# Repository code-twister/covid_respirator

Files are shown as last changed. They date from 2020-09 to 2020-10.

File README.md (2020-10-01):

# code-twister ventilator

## The idea

Following the shortages of ventilators in countries severely affected by covid 19 this project aimed to give a relatively cheap solution to help those people who have no other option.

The design itself is intended to be free for anyone to use, update, create and even sell the machines.

There are a lot of other open source ventilators to choose from, hopefully this design will also help.

DISCLAIMER: This project and all related resources are provided without any guaranties, and you should use it at your own risk. Please make sure you respect the law in your country related to medical equipment.

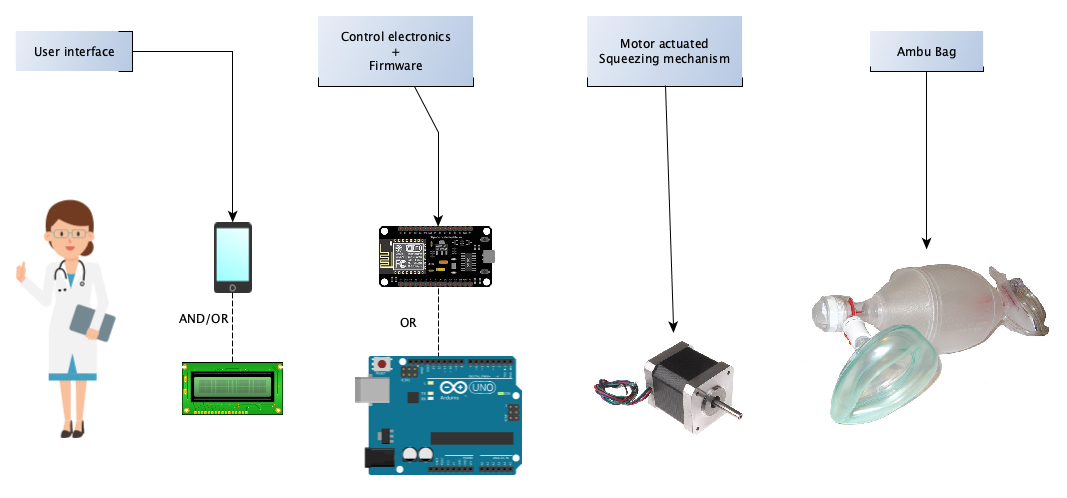
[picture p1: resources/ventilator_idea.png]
Ventilator idea The basic ventilator idea


### Things considered
 - Parts should be readily available (e.g. 3d printer parts).
 - Custom components should be 3d printable or created using common hand tools.
 - Use **ambu bag** as air delivery to make sure it's safe for patients.
 - A way to set parameters like speeds, volume, pressure limits, sigh feature.
 - Ambu bag must be easy to replace by medical personnel.

## Ventilator prototype

(http://www.youtube.com/watch?v=9s-Q_Xbm_GY "Prototype")

**Actual build:**

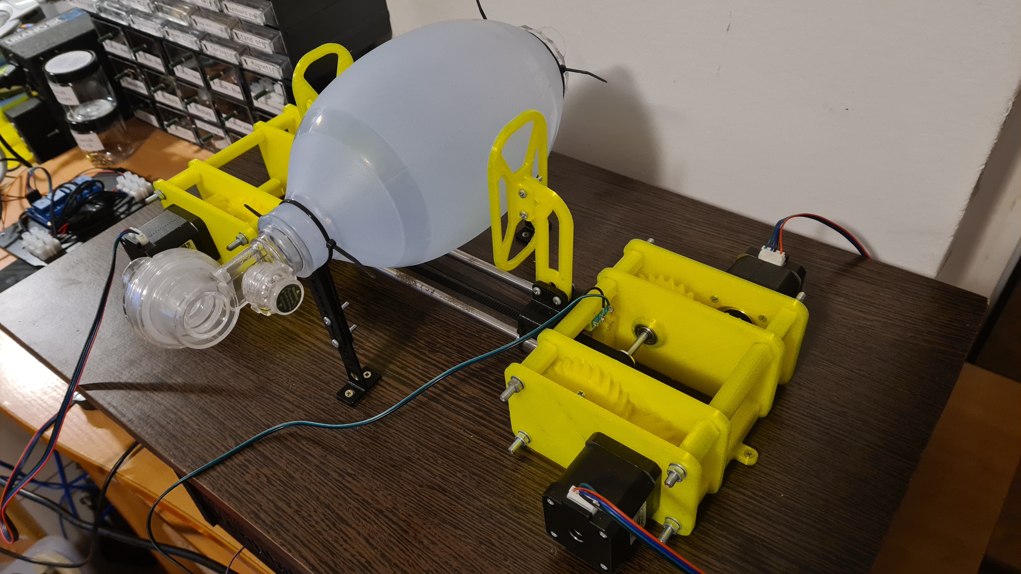
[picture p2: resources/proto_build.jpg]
Prototype build


**And a short demonstration:**

(http://www.youtube.com/watch?v=f7BWuTpa6zQ "Example prototype build")

## Parts 

Purchasable parts:

| Part name             | Count | Comments                       |
|:----------------------|------:|--------------------------------|
| Nema 17 Motor         |      4| bigger motor would work better |
| CNC Shield            |      1| one that has 4 motor drivers   |
| Pololu stepper driver |      4|                                |
| 8mm linear rail       |      2| 260mm                          |
| LM8UU bearing         |      4|                                |
| Wood board            |      1| 600x300mm                      |
| Ambu Bag              |      1|                                |
| M5 threaded rod - L1  |      8| ~ 150mm                        |
| M5 threaded rod - L2  |      2| ~ 120mm                        |
| GT2-20 Pulley         |      2|                                |
| GT2 Timing belt       |      2| ~ 400mm                        |
| 12/24V power supply   |      1| most stepper drivers can handle up to 30V |
| Arduino/NodeMCU       |      1| any microcontroller that has at least 2 digital output pins |
| 625 bearing           |      4|                                |
| M3 screws & nuts      |      ?| mostly 10mm & 15mm, longer ones are also OK |
| Wood screws           |      ?| for: feet, power supply, electronics and fixing the top mechanism to the base |
| Zip ties - 3mm        |      ?| fixing                                | 
| Legs                  |      4| I used furniture legs from hardware store but you can print them |
| Mechanical end-stop   |      1|                                | 

3D Printed parts:

| Part name                   | Count | Link                             |
|:----------------------------|------:|----------------------------------|
| Motor mounting plate 1      |      4| [download](3d_models/MountingPlate1.stl)  |
| Motor mounting plate 2      |      4| [download](3d_models/MountingPlate2.stl)|
| Small Gear                  |      4| [download](3d_models/InputGear.stl)|
| Large Gear                  |      4| [download](3d_models/OutputGear.stl)|
| Small Motor spacer          |     16| [download](3d_models/SmallMotorSpacer.stl)|
| Large Motor spacer          |      3| [download](3d_models/LargeMotorSpacer.stl)|
| Motor Mounting spacer       |      2| [download](3d_models/MotorMountingSpacer.stl)|
| Spacer with end-stop        |      1| [download](3d_models/SpacerWithEndstop.stl)|
| Shaft holder                |      2| [download](3d_models/ShaftHolder.stl)|
| Carriage Upper              |      1| [download](3d_models/CarriageUpper.stl)|
| Carriage Lower              |      1| [download](3d_models/CarriageLower.stl)|
| Arm link                    |      2| [download](3d_models/ArmLink.stl)|
| Pad                         |      2| [download](3d_models/Pad.stl)|
| Bag Holder base             |      2| [download](3d_models/BagHolderBase.stl)|
| Bag Holder slider           |      2| [download](3d_models/BagHolderSlider.stl)|
| Electronics box             |      1| Design or download an electronics box that fits your circuit |

## Example circuit

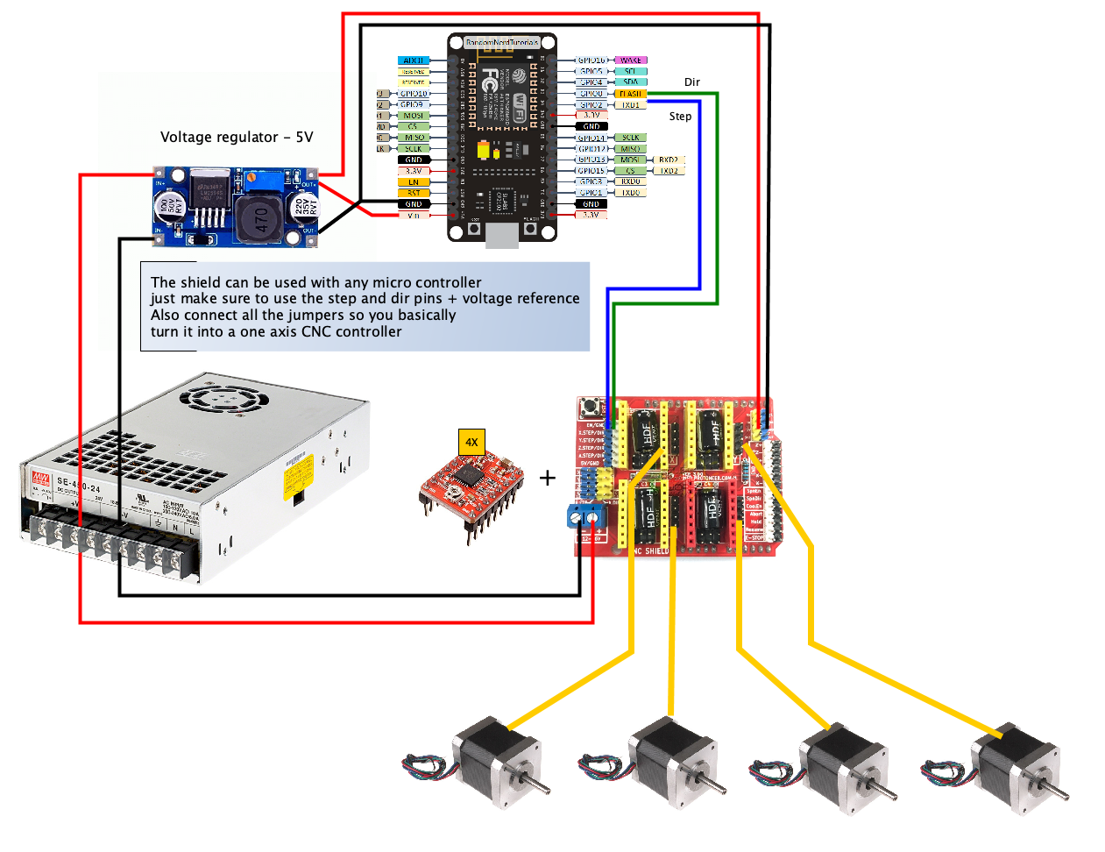
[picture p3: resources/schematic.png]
Schematic An example circuit


This is the basic circuit. It's recommended to also add an end-stop and pressure sensors on the air line. These can be directly wired to the microcontroller (no need to use the CNC shield).

## Tips

Although the circuit is using the CNC shield, you don't need to upload a GRBL firmware, just make sure to use a pololu stepper driver with the correct pins configured.

The mechanism relies on the fact that all motors are mechanically connected. This means that all the forces are split equally. The motors and drivers should have the same specs, also you can drive them with only one set of dir and step pins.

To tension the belt: once the top mechanism is completely assembled, screw down one motor assembly and pivot the other one around the shaft holder. This will give you slack to shorten the belts. (Please make sure belts have same length, otherwise the carriages will not meet in the middle)

Don't try to make a very sturdy bag holder. The bag needs to expand and contract when squeezed. If the holder isn't flexible enough, the bag will either pop off, or the force will be added to the air resistance and stall the motors.  

## Limitations and proposed improvements

After lots of calculations, measurements I arrived at the conclusion that practice doesn't always match theory.
While the ~0.5Nm Nema 17 motors seem to just about meet the required torque output, there are some weak elements to this design.
The mounting of the large gear on the drive shaft (5mm threaded rod) and the GT2 pulley sometimes slip. 

Another issue is noise. Fixing the motors directly to the base transfers all the vibrations of the mechanism + the natural noise of the stepper motors.

If you use a pressure sensor make sure to find a working pin on the microcontroller for it first, as it may not work with all input pins.

Proposed solutions:
 * introduce larger motors (different drivers, and probably without the shield)
 * drill hole in the shaft that accepts a set screw (to avoid slipping), maybe use a larger drive shaft
 * place a rubber pad between motor mount and base to reduce vibrations.
 * add stepper silencer boards or use more expensive and efficient motor drivers.

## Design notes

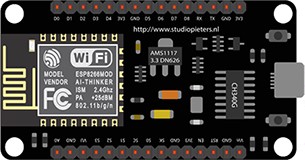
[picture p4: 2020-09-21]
resources/NodeMcu.jpeg

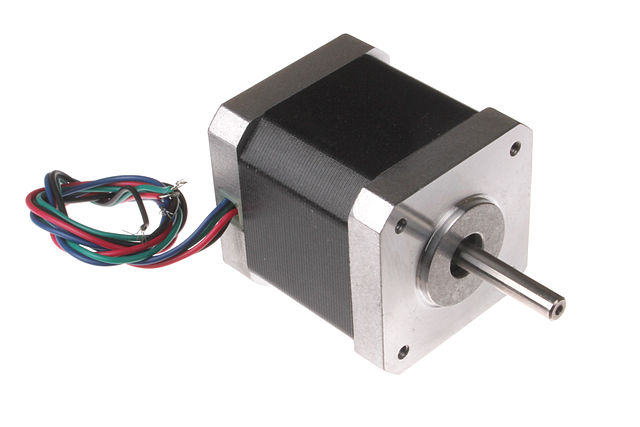
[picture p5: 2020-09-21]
resources/Nema_17_Stepper_Motor.jpg

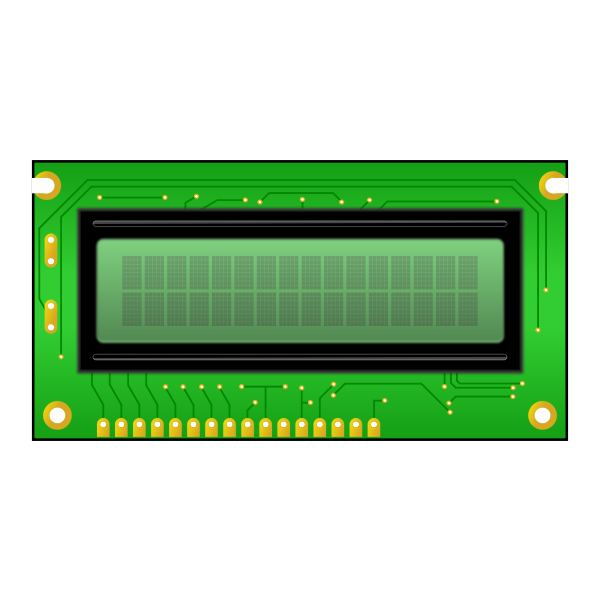
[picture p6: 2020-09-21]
resources/lcd-16x2.png

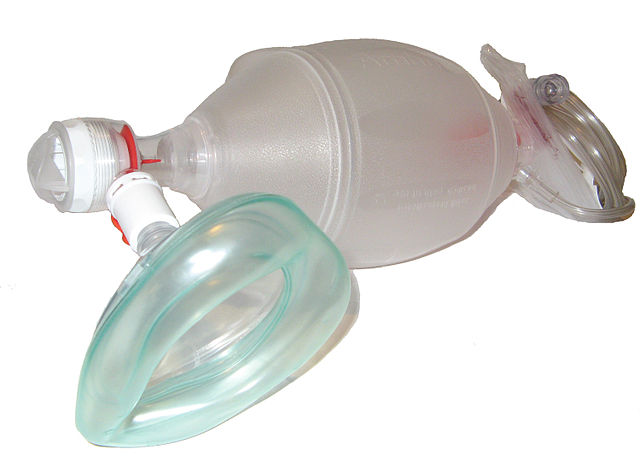
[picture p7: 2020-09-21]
resources/Ambu_Bag_valve_mask.jpg

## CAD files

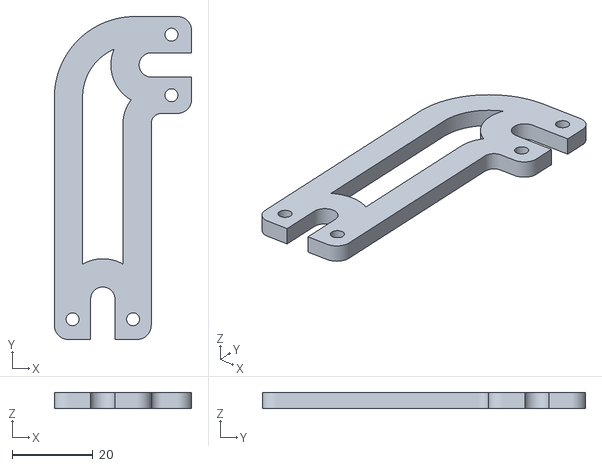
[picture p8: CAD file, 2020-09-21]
3d_models/ArmLink.stl
34.0 x 80.0 x 4.00

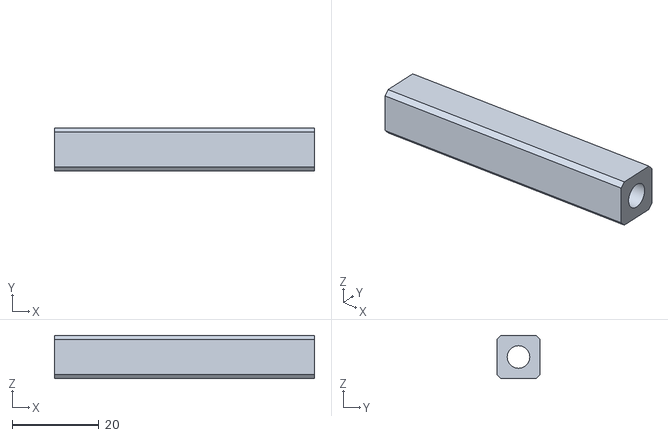
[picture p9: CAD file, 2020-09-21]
3d_models/LargeMotorSpacer.stl
60.0 x 10.0 x 10.0

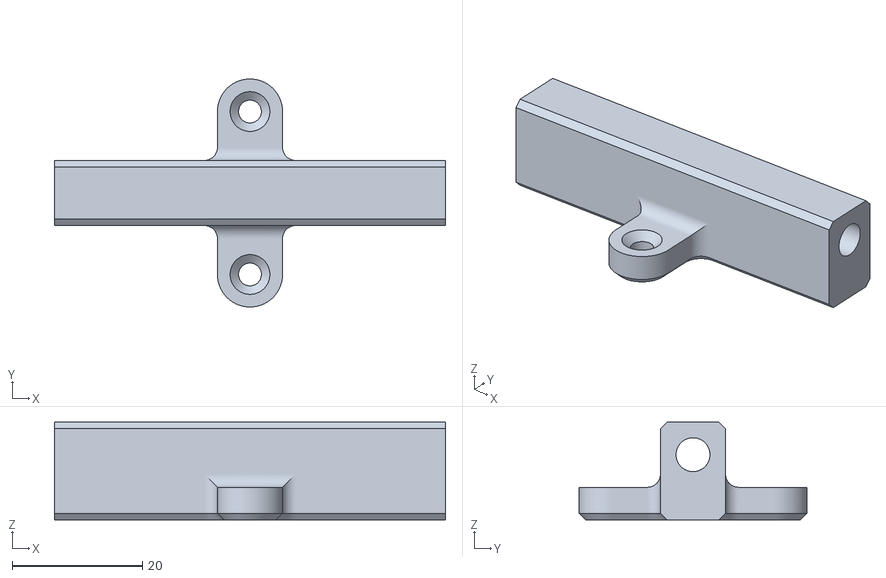
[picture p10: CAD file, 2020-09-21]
3d_models/MotorMountingSpacer.stl
60.0 x 35.0 x 15.0

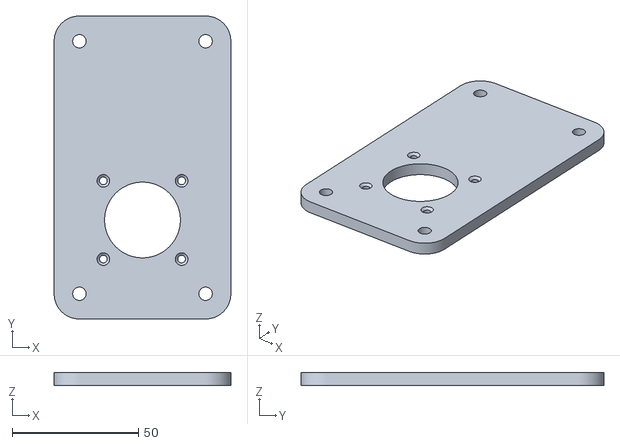
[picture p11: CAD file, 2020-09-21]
3d_models/MountingPlate1.stl
70.0 x 120.0 x 5.00

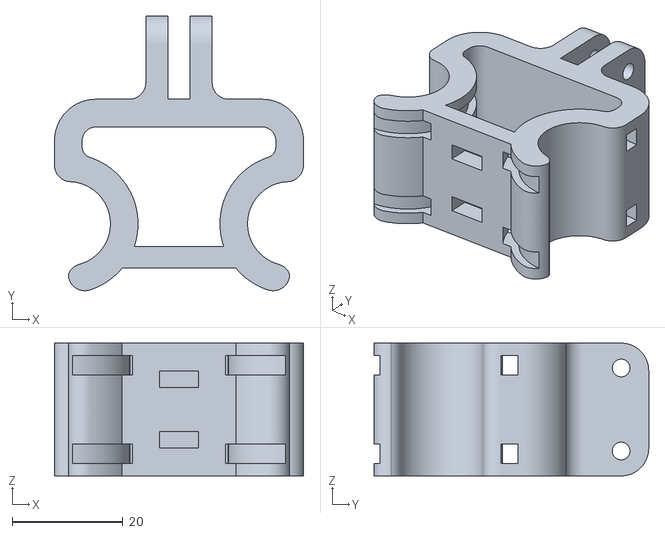
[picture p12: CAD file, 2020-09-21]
3d_models/CarriageLower.stl
45.0 x 49.6 x 24.0

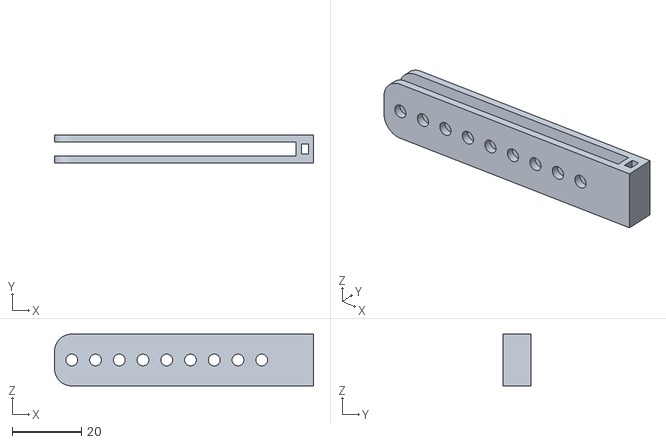
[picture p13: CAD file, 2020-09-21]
3d_models/BagHolderSlider.stl
75.0 x 8.00 x 15.0

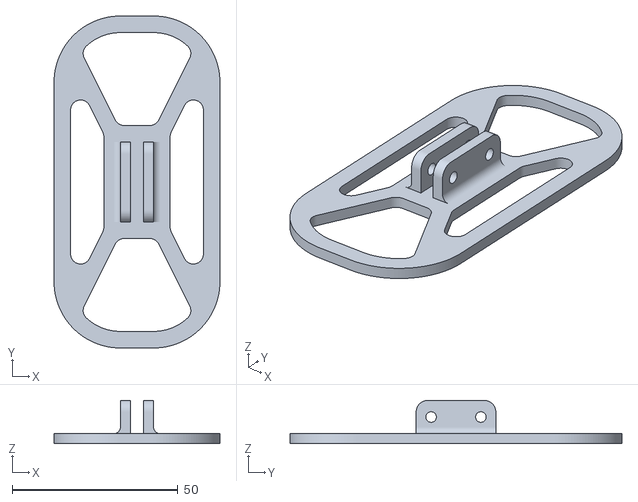
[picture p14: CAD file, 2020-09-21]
3d_models/Pad.stl
50.0 x 100.0 x 13.0

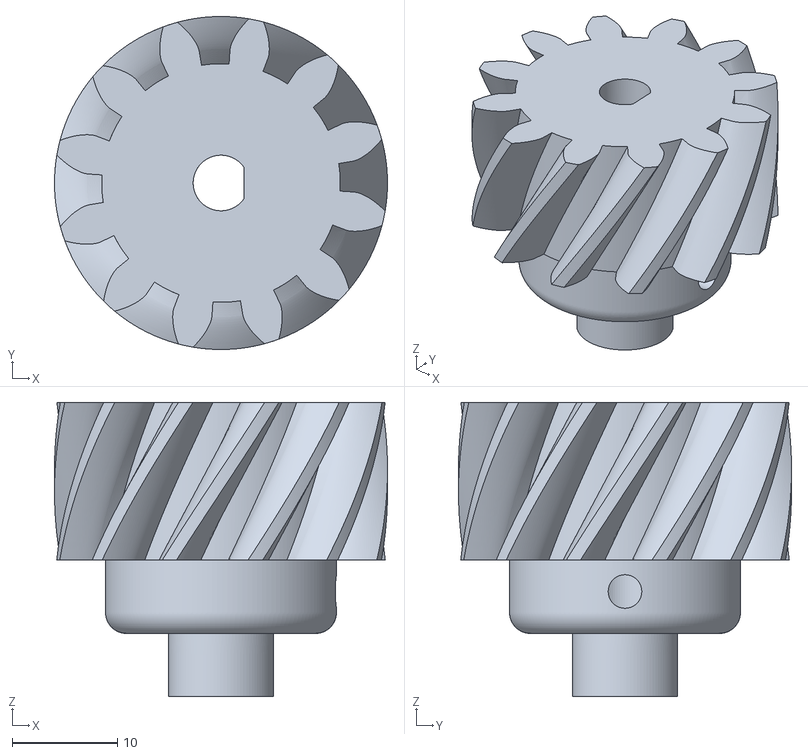
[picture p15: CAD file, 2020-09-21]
3d_models/InputGear.stl
31.7 x 31.7 x 28.0

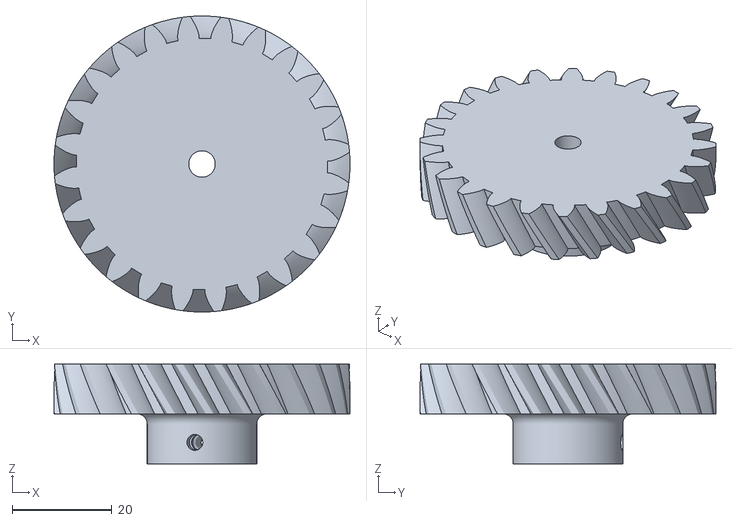
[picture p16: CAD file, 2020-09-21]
3d_models/OutputGear.stl
59.4 x 59.4 x 20.0

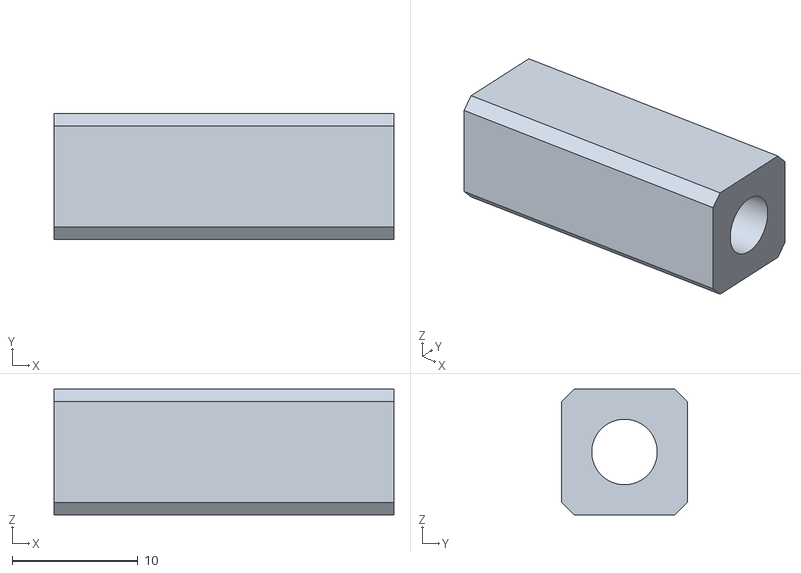
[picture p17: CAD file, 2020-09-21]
3d_models/SmallMotorSpacer.stl
27.0 x 10.0 x 10.0

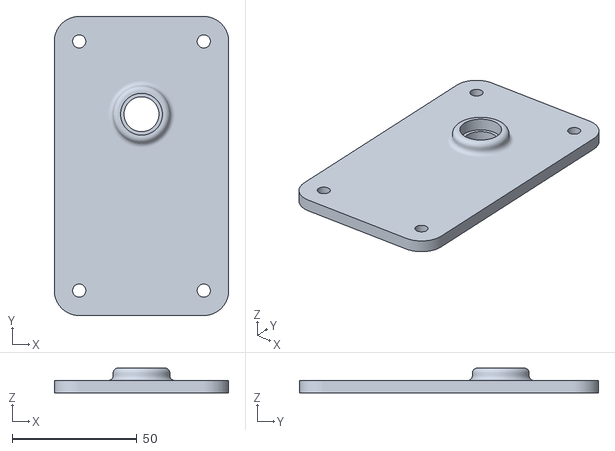
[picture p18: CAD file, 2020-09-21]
3d_models/MountingPlate2.stl
70.0 x 120.0 x 10.0

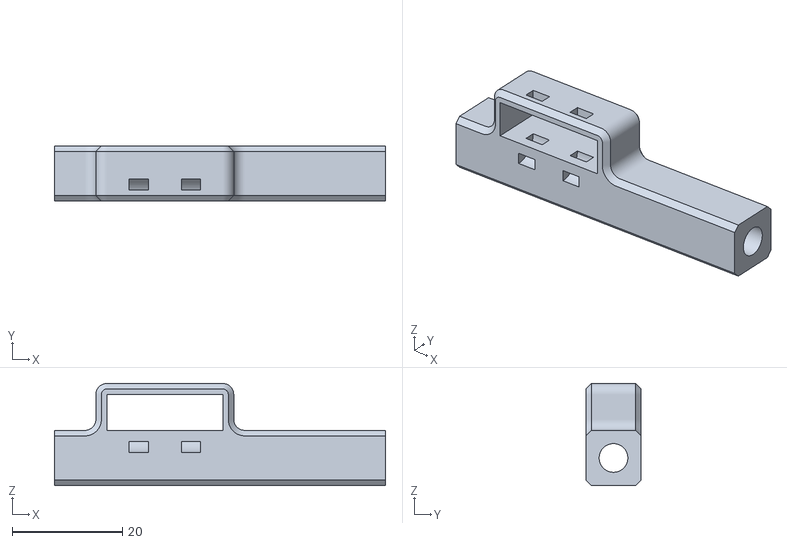
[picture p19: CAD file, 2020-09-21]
3d_models/SpacerWithEndstop.stl
60.0 x 10.0 x 18.5

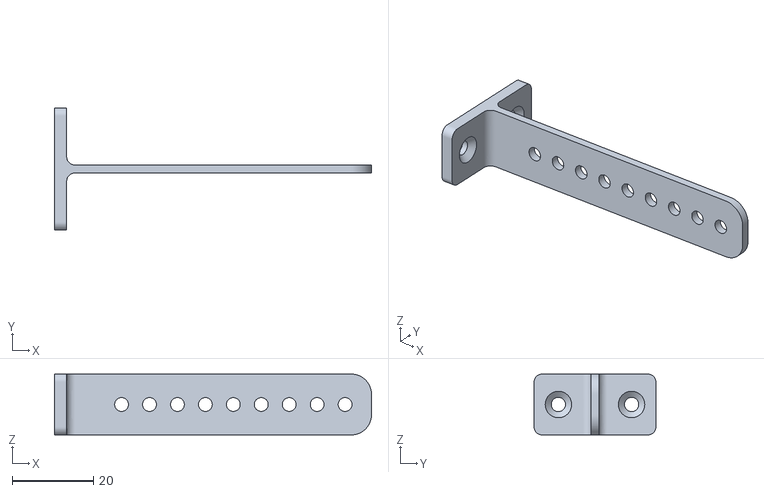
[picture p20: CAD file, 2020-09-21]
3d_models/BagHolderBase.stl
78.0 x 30.0 x 15.0

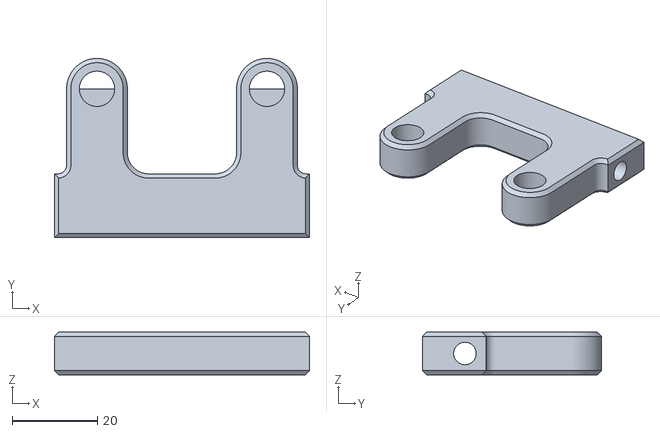
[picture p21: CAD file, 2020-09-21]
3d_models/ShaftHolder.stl
60.0 x 42.1 x 10.0

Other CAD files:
3d_models/CarriageUpper.stl
